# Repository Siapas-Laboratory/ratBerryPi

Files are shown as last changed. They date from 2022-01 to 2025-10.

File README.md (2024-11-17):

# ratBerryPi
A Raspberry Pi based system for controlling liquid-reward delivery and basic cue presentation for animal behavioral experiments. The system is customizable and programmable with Python. Functionality is provided for interfacing with the hardware either locally on the Pi or remotely from a client device. We also provide an additional Python package, [pyBehavior](https://github.com/nathanielnyema/pyBehavior) which contains tools for building GUIs to interface with the system (remotely or locally) and for developing behavioral protocols which leverage the hardware.

## Overview
ratBerryPi was built for the general class of behavioral paradigms that involve an animal collecting a liquid reward from one of many end points. The system is built around a modified version of the open source [Poseidon Syringe Pump](https://pachterlab.github.io/poseidon/), which we use to supply fluid as reward to any of multiple reward end-points via a manifold of 3-way stopcocks with luer connectors and an array of media isolation solenoid valves. One valve on the manifold is connected to a reservoir which can be used to intermittently refill the syringe without unloading and reloading it. The reward end-points in this system are modules that are each fitted with a lickometer, speaker and LED. The reward modules plug into a central interface that sits as a HAT on the Raspberry Pi controlling the system. In theory, up to 32 modules can be connected to a given pi by stacking 4 interface HATs. All peripherals are accessible and programmable through a Python class we've defined called the RewardInterface. Users may access this interface either remotely or locally (see [Usage](#usage)). The codebase was developed with flexibility and configurability in mind such that skilled users may modify the hardware and software to meet their needs (see [Software Overview](docs/software_overview.md) and [Hardware Overview](docs/hardware_overview.md)).

[***PICTURE HERE***]

## Getting Started
In this repository we provide stl files for our modified version of the syringe pump and manufacturing files for printing our custom PCBs which control all peripherals. For build instructions use the following links:

- [Hardware Assembly](docs/hardware_assembly.md)
- [PCB Ordering](docs/pcb_ordering.md)
- [Electronics Assembly](docs/electronics_assembly.md)

### Software Installation - (Raspberry Pi)
Clone this repository then follow these steps to setup a raspberry pi for use with ratBerryPi:

1. If you haven't already, install miniforge3 by downloading using the appropriate installer which can be downloaded from [here](https://github.com/conda-forge/miniforge?tab=readme-ov-file#download).

2. Create a conda environment using the environment.yml file provided in this repo and activate it by running the following from the project directory:

```
conda env create -f environment.yml
conda activate ratBerryPi
```

3. Run the following to configure the pi for use with the adafruit-blinka library (modified from [here](https://learn.adafruit.com/circuitpython-on-raspberrypi-linux/installing-circuitpython-on-raspberry-pi)):

```
pip install --upgrade adafruit-python-shell
curl https://raw.githubusercontent.com/adafruit/Raspberry-Pi-Installer-Scripts/master/raspi-blinka.py| sudo -E env PATH=$PATH python -
```

4. After the reboot, re-navigate to the project directory, re-activate the conda environment and run the following to finish the installation:

```
pip install '.[pi]'
```

#### If using with pyBehavior
If interfacing with ratBerryPi through [pyBehavior](https://github.com/nathanielnyema/pyBehavior) directly on the pi you can install pyBehavior in this environment by first cloning the pyBehavior repo and then running the following from the cloned repository:

```
conda env update --name ratBerryPi --file environment.yml
pip install .
```

### Software Installation - (Client Device)
As detailed in the Usage section below, one mode of operation of this system is to configure the raspberry pi that is connected to the hardware to function as a server that clients may connect to in order to trigger rewards or cues. For this to work, the ratBerryPi python package must also be installed on the client device. To install ratBerryPi on a client device, simply clone this repository, navigate to the cloned repository and run `pip install .` while any desired virtual environment is activated.

## Usage
There are 2 main modes of operation for the ratBerryPi. The Raspberry Pi can be configured as a server that clients on other machines may connect to in order to run commands through the RewardInterface class. Alternatively, one may write a Python program on the raspberry pi itself which creates an instance of the RewardInterface class and invokes methods of the class to run a behavioral protocol.

### Local RewardInterface

Users may interact with the ratBerryPi through an instance of the RewardInterface class as follows:

```python
from ratBerryPi.interace import RewardInterface

rpi = RewardInterface()
rpi.start()

# do something

rpi.stop()
``` 

If nothing is passed to the constructor of the class, rpi will be an instance of the RewardInterface configured according to the config file located at ratBerryPi/config.yaml in the cloned repo (see [Configuration](docs/software_overview.md/#configuration); you shouldn't need to alter the config if using the hardware we provide). The constructor can also optionally take the following parameters which can be ignored by most:

- `on` (threading.Event) - threading event object that can be used to synchronize start and stopping the interface with any other threads which may be running in your program (for an example see `ratBerryPi/remote/server.py` where we use an event to stop the interface when we stop the server)
- `config_file` - path to an alternate config file
- `data_dir` - path to a directory to save any data produced by the interface after calling the `record` method. If not specified all data is saved at `~/.ratBerryPi/data`

Several instance methods are provided through `rpi` which allow the user interact with the hardware. For a full list of these methods see the help documentation for the RewardInterface class. This documentation can be accessed from a python terminal as follows:

```python
from ratBerryPi.interface import RewardInterface
help(RewardInterface)
```

### Server-Client Mode
We provide a cli for creating either a server or a cli via the command `ratBerryPi` which can be called from the command line. To start a server on the raspberry pi, simply run the command `ratBerryPi server`. This will expose a port on the raspberry pi for clients to connect to for running commands through the reward interface and broadcasting information about the state of the device.  By default it will bind port 5562 but this can be set as needed by passing the arguments `--port`. If using an interface other than the reward interface.

Users may connect to the server programmatically by first creating an instance of the `Client` class defined in `client.py`. For example:

```python
from ratBerryPi.client import Client

host = '123.456.789' # raspberry pi ip address
port = 5562

cl = Client(host, port)
```

Once you've created the client, the 2 most important methods of this class are `run_command` and `get`. 

- `run_command` provides an interface to run commands remotely through the interface running on the server. It takes as input 2 positional arguments, the first of which is a string indicating the name of a method in the interface class to run. The second argument is a dictionary specifying keyword arguments for this function. For information on available methods see the help documentation for the RewardInterface as discussed above

- `get` provides an interface to retrieve state information from the reward interface; it takes as input a string indicating the attribute of interface class you would like to get the value of. This string should be everything that would come after the period when directly accessing an instance of the interface class. for example, if we want the position of a pump named `pump1` when using the reward interface, the request would be `'pumps["pump1"].position'`.  

Both `run_command` and `get` further take as input an optional keyword argument `channel` which allows the user to specify the name of a 'channel' for communicating with the server. These channels are simply an abstraction for a connection to the server and allow users to isolate certain types of requests to avoid cross talk. For example, I may want to create an app using the reward interface where it would be useful to spawn a thread in the background to continuously monitor the position of the pump so I can print it for the user to see. It would be useful in this case to create a new channel specifically dedicated to these requests. Behind the scenes the server keeps these channels isolated by spawning separate threads for handling requests made on different channels. To create a new channel simply use the method of the client class `new_channel` which takes as input one positional argument which is the name of the new channel.

To start a client via the cli simply run the command `ratBerryPi client`. The default behavior of this method is to connect to a server hosted locally. If you would like to connect to a ratBerryPi server from a separate client device provide the `--host` argument as well as the `--port` argument if the server is being hosted on a non-default port. This should launch a cli where you can enter method names from the reward interface as commands followed by argument names and associated arguments separated by spaces. For example, if you wanted to run the trigger_reward method for a 1 mL reward on module1,  you would enter:

```
trigger_reward module module1 amount 1
```

There are 2 special commands: `get` and `exit`. `exit` will close the connection to the server and stop the cli. `get` is the cli equivalent to the get method described above.

## Operating the Pump and Manifold
The primary interface to the pump and valves is meant to be in software, however we provide some features to control the pump and fill valve manually to help with loading and unloading a syringe. Specifically, there are 3 buttons on the interface HAT that users should be familiar with: the flush button, the reverse button, and the fill valve button. The flush button allows you to manually advance the pump carriage sled forward. The reverse buton allows you to manually advance the pump carriage sled backwards. The fill valve button allows you to manually toggle the valve that goes to the reservoir (i.e. when the fill valve button is pressed this valve is open). In theory it is also possible to manually turn the lead screw to move the carriage sled if the pump is powered down (i.e. the 12V power supply to the interface board is unplugged) however we strongly discourage operating the pump in this way. In general it should be noted that whenever the 12V power supply is unplugged or the pump is unplugged, you should re-calibrate the pump before using it for anything. To do this you can use the calibrate method ot the Reward Interface.

### Filling the lines
For optimal performance, before triggering any rewards, all lines for reward delivery must be filled with the solution to be delivered to the reward ports. The key to doing this properly is making sure there are as few air bubbles in the lines as possible. We provide a method through the RewardInterface called fill_lines which automatically fills the lines. We strongly recommend users call this method before triggering any rewards. In the pyBehavior PumpConfig widget there is a button available that calls this method. Prior to running this method, be sure to pre-fill a syringe, load it in the pump, and make sure the reservoir is full. We've also found it useful to manually push some fluid to the reservoir while the pump is loaded with the full syringe before calling `fill_lines`. ***NOTE: If you do this make sure to hold open the fill valve with the fill valve button*** Importantly, this process can only work if the syringe used for filling the lines has at least as much volume as the dead volume leading up to the reservoir. Depending on the use case, it may even be in the user's best interest to use a fairly large syringe (about 30 mL) to fill the lines and switch to a more precise syringe for the experiment itself.

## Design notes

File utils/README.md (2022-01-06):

# Desi_FallRotation-
Code + documentation of Desi's fall rotation in the Siapas Laboratory. Project entailed developing initial steps of creating a new training chamber using python, raspberry pi, stepper motor, speaker, and other related components / pieces. 

## IRBeam.py
simple piece of code that detects whether there is a break in the IR beams. There are two approaches included in the file, as noted in the comment - using the event detection function (versus the while loop approach) would be the best method to achieve flexibility in where to place event detection in the other files (especially main.py) 

### functions
def break_beam_callback(channel):
* channel = meaningless parameter, it is there so that the function can be called currently from GPIO.add_event_detect

## audio.py

generates sine wave based on certain parameter values:
* frequency (Hz)
* duration (ranges from 0.0 to <300 seconds)
* volume (ranges from 0.0 to 1.0) 
* sample rate (samples per second) 

outputs the sine wave through the audio port on the raspberry pi 

### functions 

def sine_tone(self, frequency, duration, volume=1, sample_rate=22050)
* frequency = frequency of sound output in Hz 
* duration = length of the audio 
* volume = volume of sound output, automatically set to 100% volume. 
* sample rate = samples per second, automatically set to 22050

## syringe.py 

in reality this controls the movement of the stepper motor, and there are different 
values that are set to output the desired amount.

* units     microliters or milimeters 
* amount    integer value of amount of chosen units to output 
* syringeType   3 mL or 1 mL syringe 
* stepDelay     Would not recommend changing, but it is the delay between one movement of the motor to the next 
* stepType    "Full", "Half", "1/4", "1/16", "1/32". Automatically set to "Half".
* loopNumber    Number of loops during calibration 

### functions 

def calculateSteps(self)
calculates steps based on amount, units, syringeType, stepType 

def syringeGPIOInit(self)
intializes GPIO pins of the syringe amd sets it up 

def pulseForward(self)
pulses the motor forward by just the number of steps 

def cleanupGPIO(self)
resets the GPIO pins 

## main.py
main interface file which references audio and syringe files. This is where the menu interface is built, and where calls to different functions are made. By building the other files using an object oriented programming approach, the main file can call functions on a syringe object or audio object. To run this file, navigate to its location in a terminal and simply run the file 

python main.py 

### functions 

def highTone()
plays sound output at frequency set for the high tone 

def lowTone()
plays sound output at frequency set for the low tone 

def settingsMode()
enters setting mode to adjust different values set up for the audio or syringe.
this is not as well developed. 

def experimentMode()
enters experiment mode where user has option to pulse syringe, play high tone and low tone, or enter settings mode

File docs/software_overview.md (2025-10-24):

# Software Overview
## Architecture
RatBerryPi consists of 3 layers of abstraction: the reward interface, reward modules and resources. The interface orchestrates use of all modules and resources. Resources are considered to be devices such as a syringe pump or solenoid valve that may or may not be shared accross modules. Modules are collections or resources. Importantly, the module must have associated to it a valve which can be opened to direct the flow of fluid to it. In the default use case, the interface has associated to it a set of pumps which several reward modules share. Each module has a valve, an led, a lickometer and a speaker associated to it.

**Technical Notes**
#TODO: add some info here about how the multi-speaker control is implemented in hardware and what this means for how the speakers are controlled and also the lickometer bus

## Configuration
This package includes a default configuration file `default-config.yaml` which reserves GPIO pins and pins on the GPIO expander to control up to 8 of our custom modules. Users may specify a custom configuration file by creating a file called `.ratBerryPi-config.yaml` and placing it in the home directory of the pi (i.e. the file should have path `~/.ratBerryPi-config.yaml`). At a minimum, the configuration must specify the fields `modules` and `pumps`. `modules` should should have sub-fields corresponding to module names and each sub-field should have corresponding sub-fields with configuration parameters for that module. Pump parameters should be specified equivalently under `pumps`. Below we detail necessary parameters for pump and module configuration:

### Module Configuration
Modules may be considered either using presets or from scratch. When configuring modules from scratch, users must specify the module `type` along with any relevant parameters for that module type. Default modules, for example, are specified by "type: DefaultModule" and require the following parameters

* `LEDPin`: GPIO pin that controls this module's LED
* `lickPin`: GPIO pin monitoring licks on this module
* `SDPin`:  GPIO pin that gates audio played on this module's speaker
* `valvePin`: GPIO pin that will control the valve that gates reward delivery to this module
* `dead_volume` *(optional)* : dead volume in tubing leading up to the module
* `lickBusPin`: GPIO pin that reads the interupt signal from the bus associated to this lickometer
* `pump` - the name of the pump feeding into this reward module

Note that GPIO pins on the GPIO expander must be specified by the expander's hexadecimal address first followed by the pin name (e.g `0x21:GPA0` for pin A0 on the expander at address 0x21). As noted below, `pump` and `valve_pin` are required arguments for all module types. 

Users may specify a `preset_name` to configure a module according to preset pin mappings specified in `presets.yaml`. Any parameters not specified in the preset must be specified in the config file.

#### Custom Modules
For users that would like to create custom reward modules you will need to define the module under the `ratBerryPi/interfaces/reward/modules` folder by sub-classing the BaseRewardModule class (see `ratBerryPi/interfaces/reward/modules/default.py` for an example). Importantly, the user must define a method `load_from_config` in the sub-class which should take as input a dictionary with configuration parameters for the module (such as pin mappings) and instantiate any resources the module needs as necessary. This dictionary will come from the `config.yaml` file. For any custom module type, users must specify a pump and valvePin.

### Pump Configuration

When configuring a pump, one must specify the following fields

* `port` : usb port address for communicating with the pico that controls the pump
* `lead` : lead of the lead screw in cm
* `syringeType` *(optional)* -The type of syringe that will be loaded on the pump by default. Current options include: BD1mL, BD5mL, BD10mL, BD30mL, BD50/60mL. Note, these options refer to keys in a dictionary called `syringeTypeDict` defined in the `Syringe` class in `pump.py`. Users may add additional syringes by adding new entries to this dictionary with the inner diameter of a given syringe and the maximum length the syringe can be withdrawn to when loaded on the pump (in cm).
* `fillValvePin` *(optional)* - A pin on the raspberry pi to control a valve attached to reservoir. This valve, if specified, will be used to allow fluid to be drawn into the syringe from the reservoir

### Plugins

Users may optionally specify resources that are not attached to a module which we refer to here as "plugins". Under `plugins` the user should specify unique names for each individual plugin used in the device. Under these names the user should further indicate any relevant key word arguments that would be needed to instantiate the plugin's associated class

 ## Developer Notes
 We encourage users to clone the repository and customize the code to their needs. To define a new resource sub-class the BaseResource class in the ratBerryPi/resources folder and define the class in a file in the same folder. Note, in the interest of thread safety, the BaseResource class when initialized has an attribute `lock` which is a re-entrant lock (see [here](https://docs.python.org/3/library/threading.html#rlock-objects) for details). We recommend developers to use this lock as a way to reserve resources in case multiple clients try to access it. To create a new module simply sub-class the BaseModule class under ratBerryPi/modules and define the class within a file you create in this same folder. Importantly this BaseModule class is an abstractbaseclass which expects the user to define a load_from_config method in the subclass which will configure the module instance using a config specified as a dict which is loaded from each module field within the config file. For an example see the default module. After making any changes you can reinstall the ratBerryPi by navigating to the root directory of the repo and running `pip3 install .`

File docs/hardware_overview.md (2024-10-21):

## Electronics Overview
The 2 main hardware components of the system are the interface and the modules. The interface is a HAT that sits on a raspberry pi, but often we may refer to the entire unit as the interface. Similarly when we refer to modules we are usually referring to the entire reward module unit consisting of all attached devices (lickometer, speaker, and LED). At it's core, however, the reward module is controlled by a PCB that usually is packaged with the module. This PCB has the main electronics needed to operate all devices. The interface functions as a hub for all modules to plug into and offers some additional features which we will describe below.

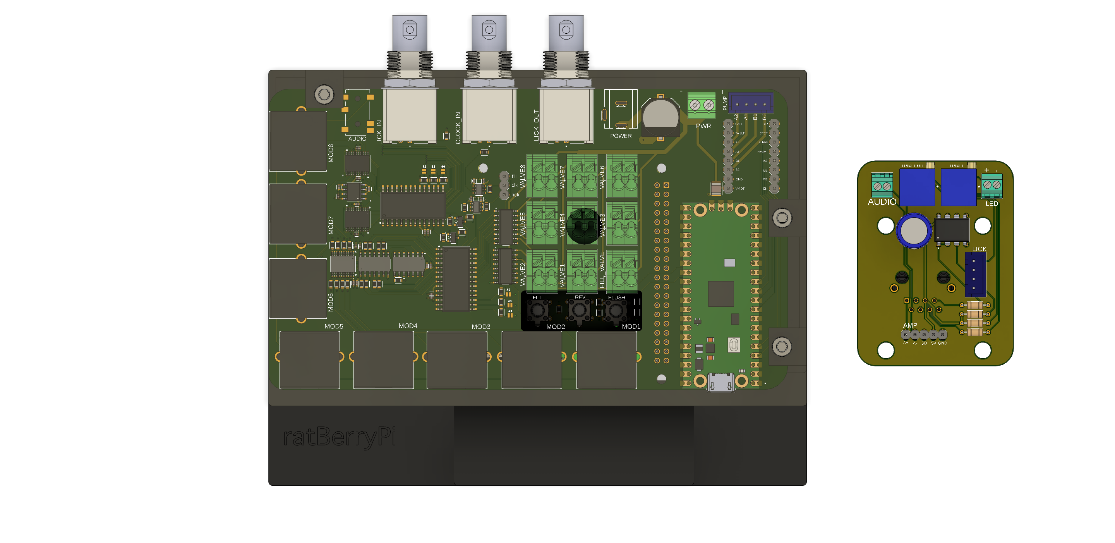
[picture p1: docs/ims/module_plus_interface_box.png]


### User Selectable I/O
Most digital I/O in the ratBerryPi system is handled through extended GPIOs provided by 2 I2C interfaces on each interface HAT. The effect is that most GPIOs on the Pi itself remain available for users program as they wish. The caveat is that there are 2 signals that could not be allocated to a slot on the I2C interfaces due to space constraints and another that needs to be read by a GPIO on the pi itself for performance reasons. Instead of hardwiring these signals to any GPIOs on the Pi we allow the user to configure them as needed. The benefit of this setup is that in the event you need to stack interface HATs, you can select different pins for each HAT as needed. The that need to be assigned to GPIOs are as follows:

* **Fill Valve Software Control** - This allows the user to set the state of the valve leading up to the reservoir in software (see [Fluid Delivery System](#fluid-delivery-system))
* **Clock Input** - see [Clock Signal](#clock-signal)
* **Lick Bus Interrupt** - all lick signals on a given interface HAT are read on the same bus of one of the I2C interfaces. There is an interrupt pin on this bus that we've configured to be LOW normally but write HIGH when when a rising edge is detected on any pins on the bus. This interrupt signal needs to be read by a designated GPIO pin on the pi itself for any licks to be registered. The idea is when this GPIO pin on the pi reads a HIGH value ratBerryPi polls the I2C interface to see which GPIO on the bus caused it. For those curious, the reason for this configuration is that the gpiozero, the library we use in python to control the GPIOs, provides an interface to configure callback functions to run very quickly on the rising or falling edge of a digital signal. We use a separate library to program the I2C interface and this library does not offer this functionality. As such the best you would be able to do otherwise is to spawn a python thread that continuously polls the state of the GPIOs on the I2C interface.

### OR'd Licks
In many setups there may be a central unit that you want to use to timestamp all events that occur during experiments. In such scenarios we offer 2 ways of getting timestamps of lick events on the clock of your timestamping unit. One is through the **CLOCK IN** port that we will discuss later. The other is through the **LICK OUT** port. This port broadcasts a 5V TTL signal which represents the result of a hardware "OR" operation over all modules on the interface. This is implemented in hardware by a cascade of pairwise logical OR gates where the inputs are the digitized lick signals. Importantly, at the last step, the OR's lick signal from the modules on a given interface is OR's with any licks provided through the **LICK IN** port. This port takes 5V logic. The result is that if you stack interface HATs or use multiple interfaces in a given setup, you can chain together multiple interfaces and the OR'd lick output of the last interface will be the OR'd licks over all modules. 

### Clock signal
One can use the software interface provided through this repo to log relevant events that occur. One method of synchronizing this datastream with datastreams on other systems is a method detailed in the OpenEphys documentation. Briefly, the idea is to timestamp a common clock signal on all devices. This signal is some digital signal with known temporal structure that can be used to map timestamps on all devices to a common clock. We support use of such a system with the **CLOCK IN** port. Users may plug such a clock signal (5V logic) into this connector and an event called clock will be logged with respect to the pi's system clock on the rising edge of all pulses detected on this port. Considering all other events logged through ratBerryPi are also logged against system clock, you can use the timestamps of these clock events to remap system clock of the pi against a common clock for all relevant devices.

### Stackable HATs
This feature has not been tested as yet, but in principle the interface HATs are designed to be stackable. When stacking HATs, the following should be taken into consideration:
* Be sure to daisy chain 12V power to all stacked HATs. The PWR screw terminal is there for this purpose
* Update the I2C address on all stacked HATs to be unique. This can be done using the address select jumpers (A0-A2 and B0-B2) on the interface HAT. Jumping any pads together sets that bit in the I2C address to 1. By default, (A0=0, A1=0, A2=0) and (B0=1, B1=0, B2=0).

### Audio
All modules have a screw terminal to plug in a speaker. Audio is provided to the modules from a single audio source which can be plugged in through the headphone jack on the HAT. This audio source can either be an audio HAT (specifically the [Innomaker HIFI DAC Pro HAT](https://www.amazon.com/Raspberry-DAC-Pro-ES9038Q2M-Resolution/dp/B0B2DJZTSF)) or the pi itself if using a Raspberry Pi 4. Importantly if using the Pi audio, you will need to amplify this audio on the level of the module. For this you can use the PAM8302 Class D Amplifier. There is a designated spot on the module PCB for it. Instead of plugging the speaker into the AUDIO screw terminal, you can use the output of the PAM8302. 

It's worth noting that because audio in this system is provided by a single source, it would not be possible to play different audio on different speakers. You may however, play the same audio on a subset or one of many speakers. This is handled by an onboard analog switch which directs the audio input to the desired end point.

## Fluid Delivery System
They main components of the fluid delivery system are the syringe pump, the valves that lead up to each reward module, the valve that leads up to the reservoir (the fill valve), the reservoir and the manifold of 3-way stopcocks that all valves are mounted to. 

![alt text]()

Many of these components are there to enable automatic refilling of a syringe without the need for unloading, However, the fundamental function of the system, namely delivering reward to a specified module, is supported primarily by the valves for each module and the pump. In practice, this is what a reward delivery looks like in this system:

1. A GPIO pin is set to a HIGH state in order to open the valve for a specified module
2. We wait a set period of time for the valve to actually open.
3. The pump advances to perfuse the requested reward amount.
4. We wait for a set period of time to ensure the entire reward amount has made it to the module (this is necessary because any compliance in the lines means that reward delivery is not instantaneous)
5. The GPIO pin associated to the valve is set to LOW to close the valve.
6. We wait to make sure the valve is closed.

Whenever we need to refill the syringe this is accomplished by closing all valves except the fill valve, opening the fill valve, and running the pump in reverse to draw fluid from the reservoir into the syringe. We added a clamp to the pump to allow the syringe to be secured in place to avoid significant slack when switching between reversing and advancing the pump. However, to be safe, a small volume is pumped to the reservoir before any reward delivery after the pump was in reverse.

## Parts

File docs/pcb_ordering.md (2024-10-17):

# Guidelines For PCB Ordering
Our manufacturer of choice for all PCB's to date has been JLCPCB. The manufacturing files provided are geared towards a smooth checkout process through JLCPCB. There are 2 types of PCBs that need to be built for this project: the interface HAT and the module PCB. Our recommendation is to get as much of the interface HAT assembled by JLCPCB as possible because there are many components and many of them are surface mount. The module PCBs on the other hand can be assembled as needed, and as such it should be sufficient (and more cost effective) to order these boards unassembled and solder the components to them yourself.

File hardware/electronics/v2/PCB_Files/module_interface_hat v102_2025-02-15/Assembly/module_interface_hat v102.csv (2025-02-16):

Qty | Comment | Designator | Footprint | JLCPCB Part #
10 | 0.1µF | C3, C4, C5, C10, C12, C17, C20, C21, C22, C23 | CAPC1005X60 | C361203
9 | 100kΩ | R3, R7, R8, R9, R10, R11, R12, R13, R14 | RESC1608X60 | C2139679
1 | 100µF | C2 | CAPAE1030X1050N | C2843277
1 | 100µF | C1 | CAPC3225X135 | C6120014
14 | 10kΩ | R19, R20, R21, R22, R23, R24, R26, R28, R29, R30, R31, R36, R38, R39 | RESC1608X60 | C2139679
4 | 10µF | C9, C11, C18, C19 | CAPC1005X60 | C15525
1 | 1727010 | PWR | 1727010 | C89123
9 | 1984963 | FILL_VALVE, VALVE1, VALVE2, VALVE3, VALVE4, VALVE5, VALVE6, VALVE7, VALVE8 | PHOENIX_1984963
3 | 1µF | C6, C7, C8 | CAPC1005X60 | C3015153
13 | 22kΩ | R1, R2, R4, R5, R6, R15, R16, R17, R18, R32, R33, R34, R35 | RESC1608X60 | C209074
2 | 50Ω | R25, R27 | RESC1608X60 | C830222
2 | ADG1434YRUZRU_20_ADI-L | U9, U10 | RU_20_ADI-L | C408906
1 | B4B-XH-A | PUMP | B4B-XH-A | C594232
4 | BSS138 | Q1, Q2, Q3, Q4 | SOT95P240X111-3N | C78284
3 | CONBNC002 | CLOCK_IN, LICK_IN, LICK_OUT | LINX_CONBNC002 | C2837588
1 | DC-005-2.5A-2.0 | POWER | DC-005-2.5A-2.0 | C319099
8 | HC-RJ45-5JA-1-4 | MOD1, MOD2, MOD3, MOD4, MOD5, MOD6, MOD7, MOD8 | HC-RJ45-5JA-1-4 | C3000174
1 | MAX1044ESA-T | U11 | SOIC127P600X175-8N | C140450
2 | MCP23017 | IC1, IC2 | SOIC127P1030X265-28 | C47023
1 | PINHD-1X3 | JP3 | 1X03 | C3327863
2 | PINHD-1X8 | JP1, JP2 | 1X08 | C5224027
1 | PJ-3420-A-SMT | AUDIO | PJ-3420-A-SMT | C319102
1 | SC0915 | U2 | MODULE_SC0915 | C7203002
3 | SKHHQYA010 | FILL_BTN, FLUSH, REV | SKHHQYA010 | C470257
1 | SN74HCS244QPWRQ1TSSOP20_4P4X6P5_TEX | U1 | TSSOP20_4P4X6P5_TEX | C2864779
2 | SN74HCT32DRD14 | U3, U4 | D14 | C6781
2 | ULN2003ADRD0016A_N | U5, U6 | D0016A_N | C7512

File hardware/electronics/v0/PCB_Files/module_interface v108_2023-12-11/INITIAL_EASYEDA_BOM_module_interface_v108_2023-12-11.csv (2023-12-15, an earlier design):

ID | Name | Designator | Footprint | Quantity | Manufacturer Part | Manufacturer | Supplier | Supplier Part | Price
1 | B4B-XH-A | PUMP | B4B-XH-A | 1
2 | HIF3FC-16PA-2.54DSA_71_ | SD,LED,PUMP_CTL,VALVE_CTL | SHDR16W56P254_2X8_2782X850X950 | 4
3 | CONBNC002 | LICK_OUT,LICK_IN | LINX_CONBNC002 | 2
4 | 22kΩ | R1,R2,R4,R5,R6 | RESAD724W46L381D178B | 5
5 | 61200621621 | J3 | 61200621621 | 1
6 | ULN2003ADRD0016A_N | U5,U6 | D0016A_N | 2
7 | SN74HCT32DRD14 | U3,U4 | D14 | 2
8 | 1727010 | REV_BTN,FILL_VALVE_BTN,FLUSH_BTN,VALVE1,VALVE2,VALVE3,VALVE4,VALVE5,VALVE6,VALVE7,VALVE8,FILL_VALVE | 1727010 | 12
9 | HC-RJ45-5JA-1-4 | MOD1,MOD2,MOD3,MOD4,MOD5,MOD6,MOD7,MOD8 | HC-RJ45-5JA-1-4 | 8
10 | PJ-3420-A-SMT | AUDIO | PJ-3420-A-SMT | 1
11 | DC-005-2.5A-2.0 | POWER | DC-005-2.5A-2.0 | 1
12 | X6511WVS-13H-C60D48R2 | U$12 | X6511WVS-13H-C60D48R2 | 1
13 | CAPAE830X1050N | C2 | CAPAE830X1050N | 1
14 | PINHD-1X8 | JP1,JP2 | 1X08 | 2

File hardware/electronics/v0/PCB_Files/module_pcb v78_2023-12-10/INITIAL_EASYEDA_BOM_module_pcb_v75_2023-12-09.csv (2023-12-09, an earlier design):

ID | Name | Designator | Footprint | Quantity | Manufacturer Part | Manufacturer | Supplier | Supplier Part | Price
1 | 2828XX-2282834-2 | LED | TERMBLK_254-2N | 1
2 | B4B-XH-A | LICK | B4B-XH-A | 1
3 | PINHD-1X5 | AMP | 1X05 | 1
4 | 1kΩ | R4 | PV36P | 1
5 | 220Ω | R1 | RESC1608X60 | 1
6 | 22kΩ | R2 | RESC1608X60 | 1
7 | 68Ω | R3 | RESC1608X60 | 1
8 | 5557969-1 | J1 | TE_5557969-1 | 1

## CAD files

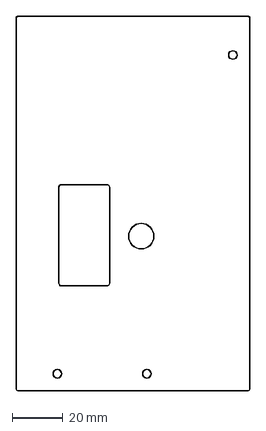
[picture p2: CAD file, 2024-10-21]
hardware/3Ddesigns/dxf/interface_box_lid.dxf
92.4 x 148.1 mm

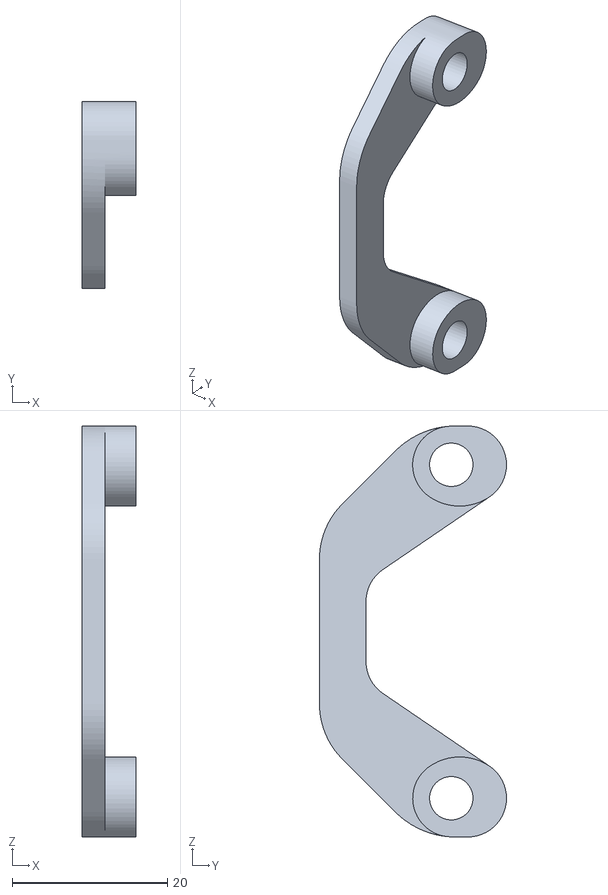
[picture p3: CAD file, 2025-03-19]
hardware/3Ddesigns/stl/pump_syringe_clamp.stl
7.00 x 24.1 x 53.0

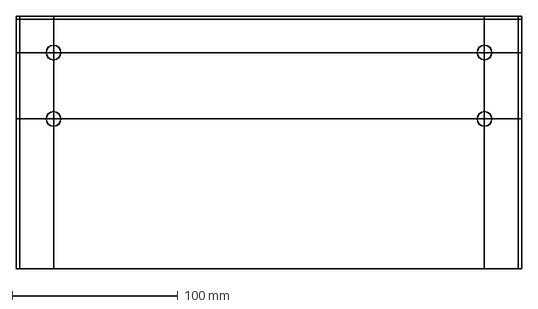
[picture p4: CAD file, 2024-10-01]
hardware/3Ddesigns/dxf/wall_sheet_6x12in.dxf
304.8 x 152.4 mm

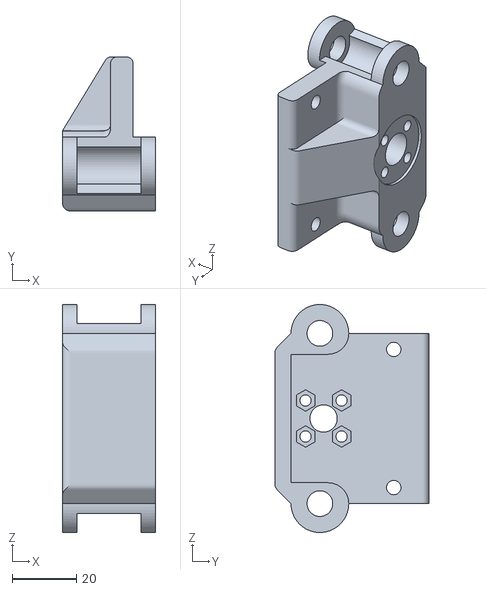
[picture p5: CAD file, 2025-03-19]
hardware/3Ddesigns/stl/pump_carriage_sled.stl
29.0 x 48.0 x 71.0

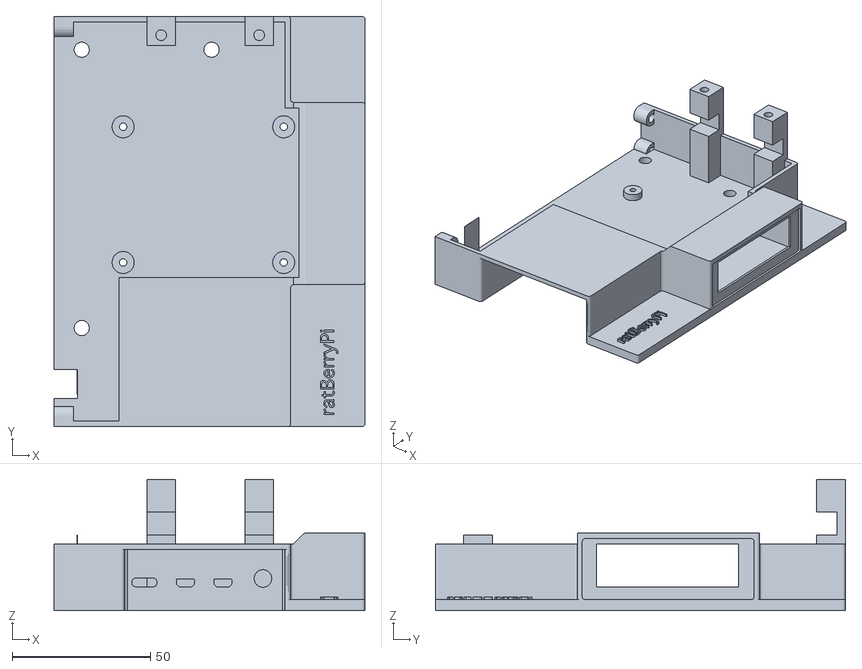
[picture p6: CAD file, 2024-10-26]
hardware/3Ddesigns/stl/interface_box_base.stl
112.3 x 148.1 x 47.4

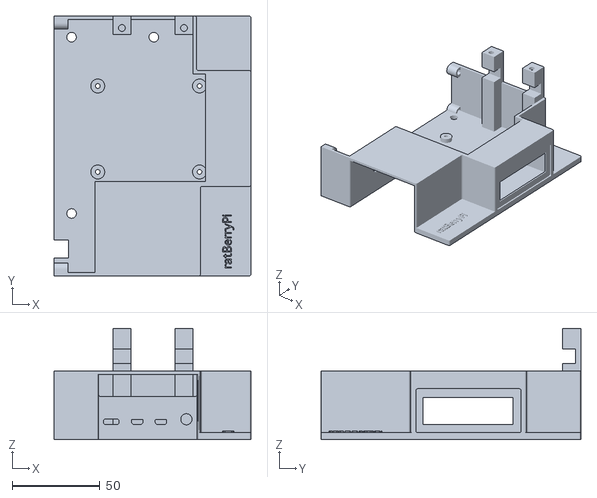
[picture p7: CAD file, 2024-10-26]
hardware/3Ddesigns/stl/interface+audio_box_base.stl
112.3 x 148.1 x 63.4

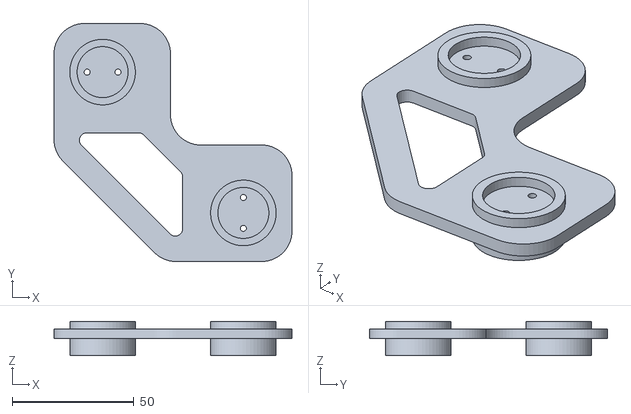
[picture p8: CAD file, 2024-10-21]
hardware/3Ddesigns/stl/2valve_mount.stl
97.9 x 97.9 x 14.0

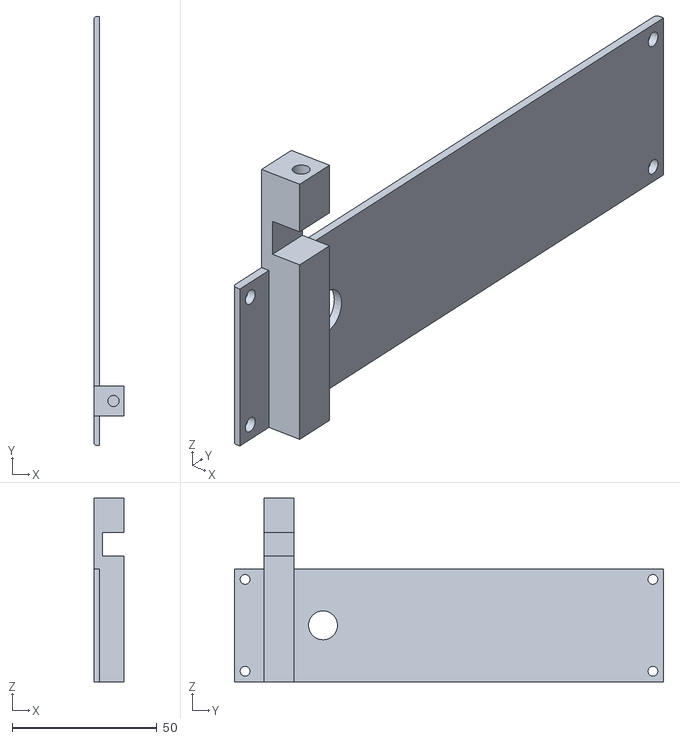
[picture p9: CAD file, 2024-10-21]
hardware/3Ddesigns/stl/interface+audio_box_back.stl
10.4 x 148.1 x 63.4

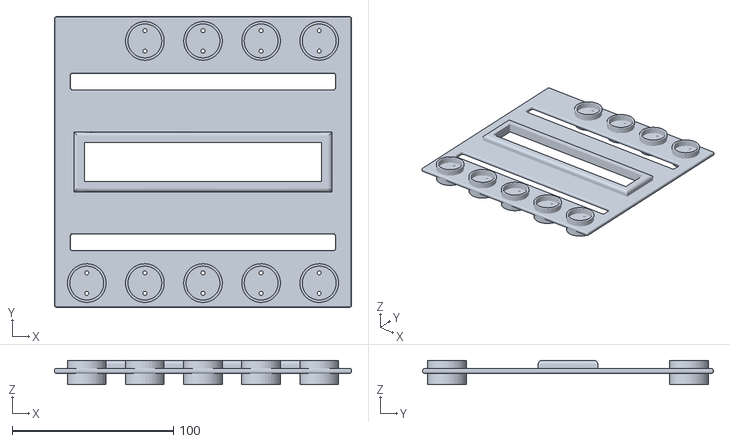
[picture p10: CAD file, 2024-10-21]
hardware/3Ddesigns/stl/manifold_mount.stl
184.0 x 180.0 x 15.0

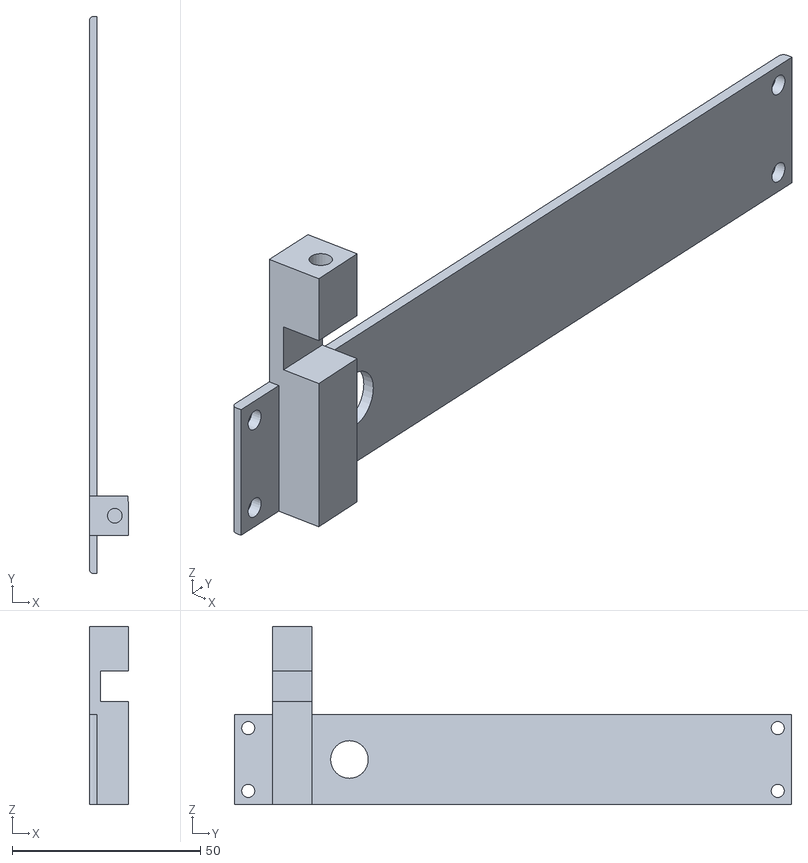
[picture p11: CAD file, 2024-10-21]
hardware/3Ddesigns/stl/interface_box_back.stl
10.4 x 148.1 x 47.4

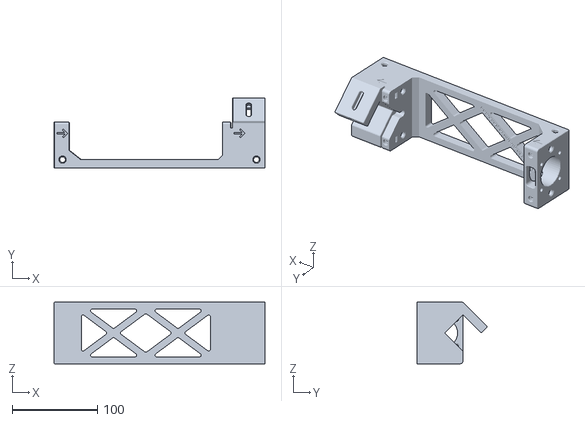
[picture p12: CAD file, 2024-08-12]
hardware/3Ddesigns/stl/pump_base.stl
247.0 x 82.3 x 72.0

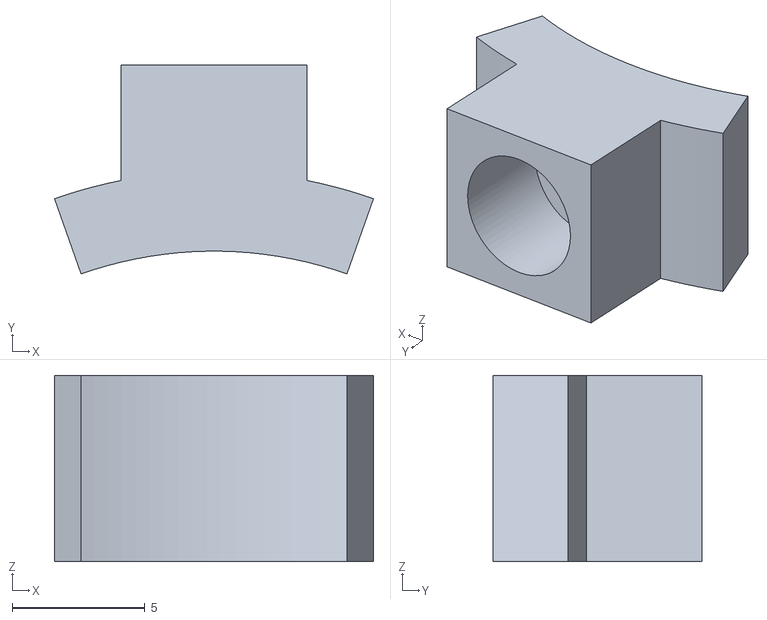
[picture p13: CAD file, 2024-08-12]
hardware/3Ddesigns/stl/pump_syringe_brace.stl
12.0 x 7.86 x 7.00

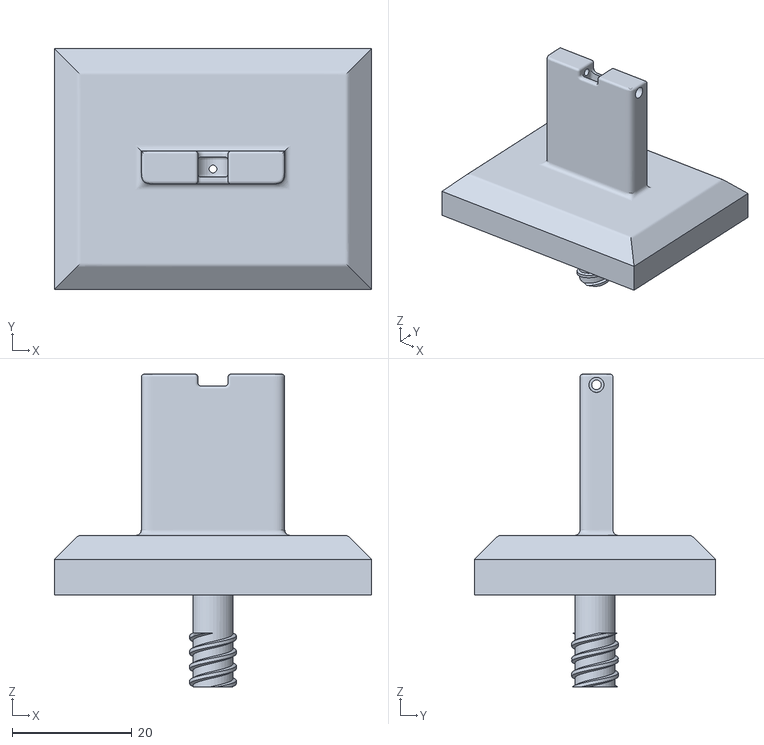
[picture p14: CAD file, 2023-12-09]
hardware/3Ddesigns/stl/lickometer_mouse.stl
53.0 x 40.3 x 52.4

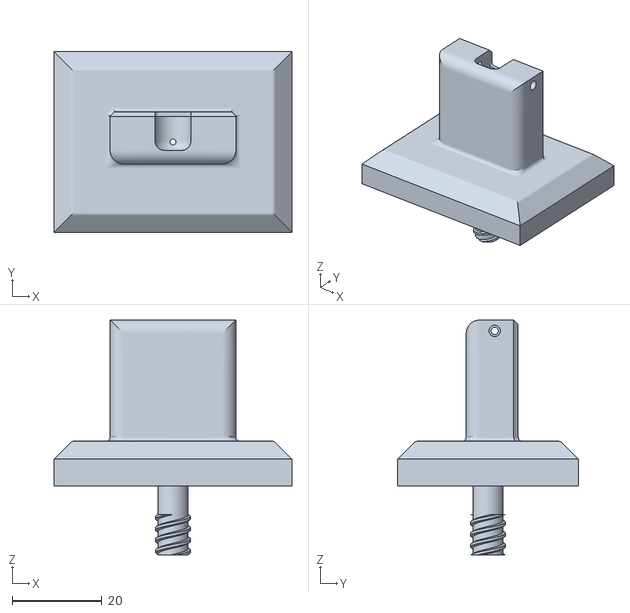
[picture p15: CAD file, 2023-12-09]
hardware/3Ddesigns/stl/lickometer_rat.stl
53.0 x 40.3 x 52.4

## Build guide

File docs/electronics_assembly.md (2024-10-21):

## Interface HAT
### Required Components
* Assembeld interface HAT + additional components that could not be assembled by the PCB manufacturer
* DRV8825 stepper motor driver (x1)
* Raspberry Pi (≥4)
* Male to Male Audio Cable (optional)
* [Innomaker HIFI DAC Pro Hat](https://www.amazon.com/Raspberry-DAC-Pro-ES9038Q2M-Resolution/dp/B0B2DJZTSF) (optional)
* 16 mm standoffs (x7) + nuts (x4)
* 10mm long M2.5 socket head screws
* Female to Female jumper
* USB cable
* printed [interface box](../hardware/3Ddesigns/stl/interface_box_base.stl) and [back](../hardware/3Ddesigns/stl/interface_box_back.stl) (if using the audio hat use this [box](../hardware/3Ddesigns/stl/interface+audio_box_base.stl) and [back](../hardware/3Ddesigns/stl/interface+audio_box_back.stl))
* M3 threaded inserts

### Assembly Steps
*Flashing Pump Code to the Pico*

In order to test out the electronics at the end we will need to have the pico firmware loaded. This is best done on a device other than the pi. We'll follow the steps detailed [here](https://randomnerdtutorials.com/programming-raspberry-pi-pico-w-arduino-ide/) to flash [pump control code](../pico/pump_control/pump_control.ino) to flash the code to the pi using the Arduino IDE.

1. Install the Arduino IDE on the device you will use to flash the code. 
2. Navigate to either Settings or Preferences depending on your OS.
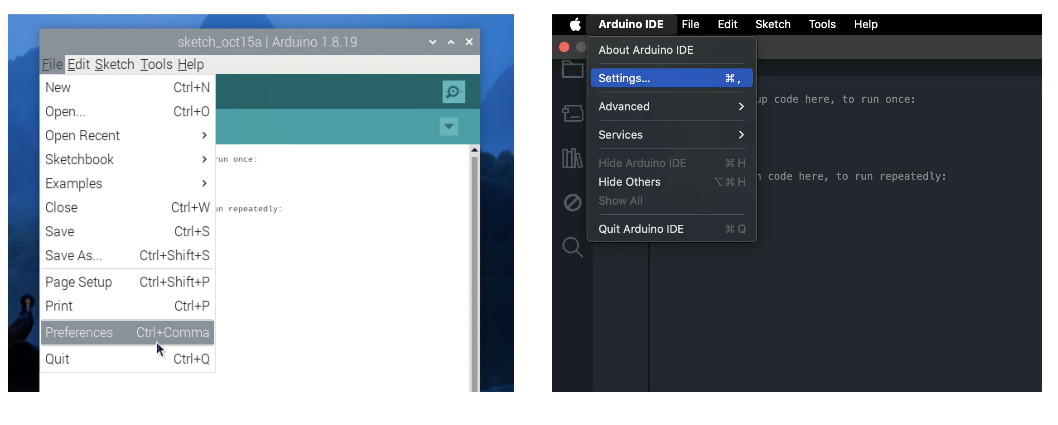
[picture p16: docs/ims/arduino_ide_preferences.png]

3. Enter the following URL in the "Additional Board Managers" field:
```
https://github.com/earlephilhower/arduino-pico/releases/download/global/package_rp2040_index.json
```
4. Go to **Tools > Board > Boards Manager**
5. Search for “pico” and install the Raspberry Pi Pico/RP2040 boards
6. Open the [pump control code](../pico/pump_control/pump_control.ino) in the IDE.
7. While the Raspberry Pi is unplugged, go to **Tools>Boards** and select Raspberry Pi Pico.
8. Hold the BOOTSEL button on the Pico while plugging it into your device.
9. Open the drop-down menu at the top and select "Select other board and port...". From here select the Rasperry Pi Pico as your board and "UF2 Board UF2 Devices" as the port. You may need to check the box that says "Show all ports"
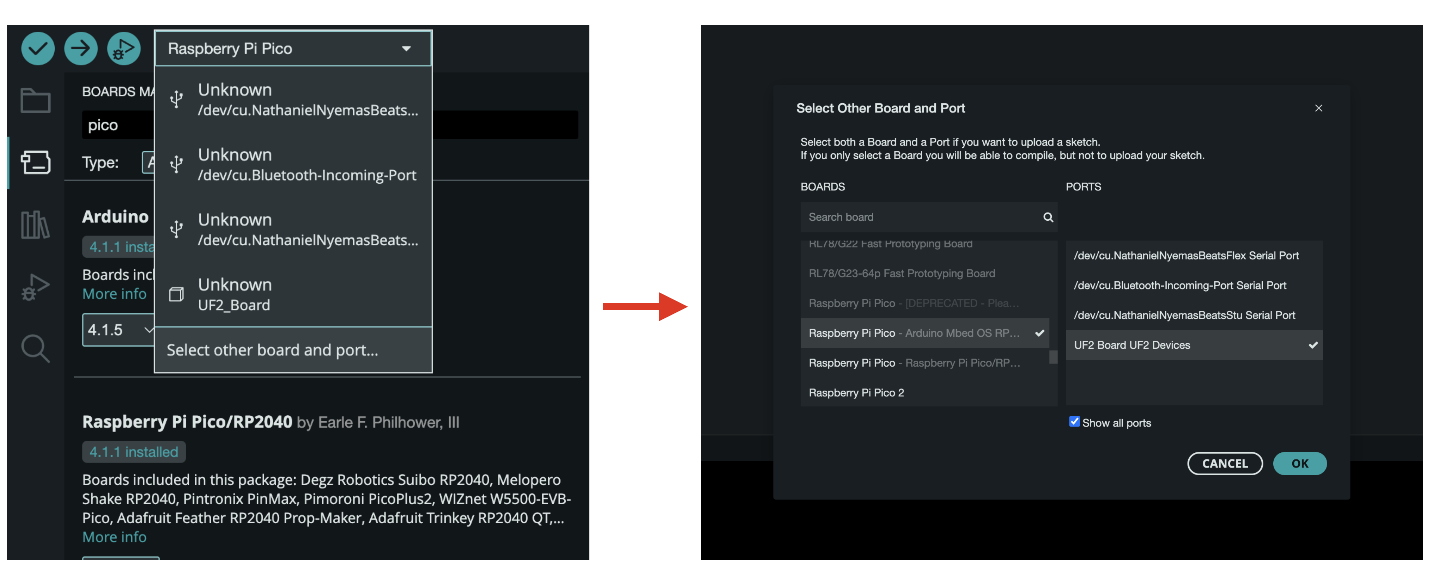
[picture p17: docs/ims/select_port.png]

10. Finally click the arrow at the top to flash the code to the Pico.


*Seting up the PCB*

1. Solder any components not soldered by the PCB manufacturer. The v1 PCB unfortunately does not have labels for all components on the board so we show the labels below. You can match component names to the part itself using the BOM for the PCB assembly job. Importantly, resistors are not labeled in this image as we generally recommend at least having these mounted by your manufacturer. (*NOTE: For all ICs the dot indicates the top left corner*)
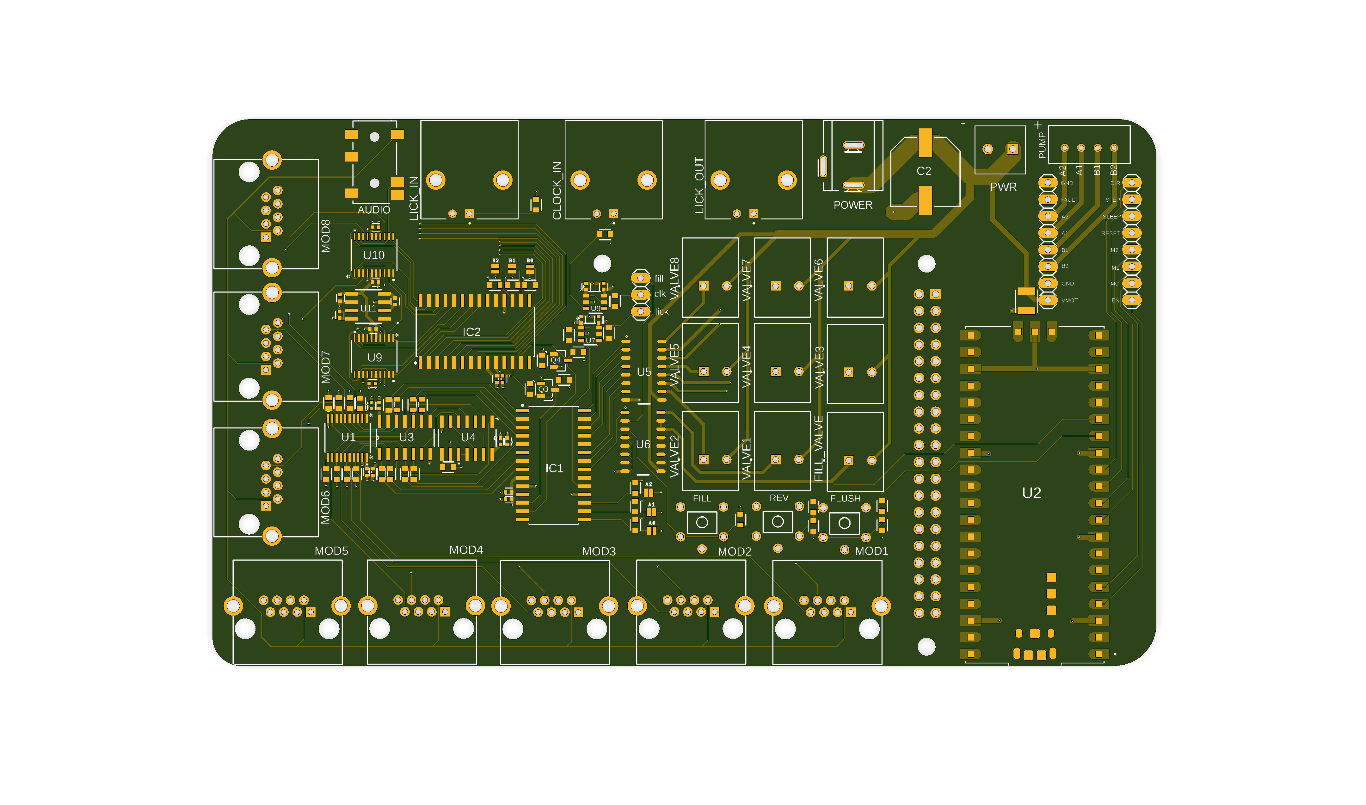
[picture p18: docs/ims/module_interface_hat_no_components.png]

2. Plug the stepper motor driver in the appropriate slot on the interface HAT being careful to match the pins correctly.
3. Now we will attach the components to the pi. The pi should be turned off at this stage. If Audio is needed plug in the audio hat first followed by the assembled interface HAT. Connect the audio hat to the interface HAT additionally by an audio cable (use the headphone jack of the audio hat). Use standoffs as needed.
4. Set all M# threaded inserts in place on the printed box parts using a soldering iron
4. Secure the Pi to the printed interface box base with M2.5 screws.
5. Screw on the back with M3 screws.
6. Power on the Pi first by plugging in the Pi power supply, then power on the Interface by plugging in the 12V supply.
7. Use a multimeter to set VREF of the stepper motor driver to 1V such that the max current output will be limited to 2A. The steps to do this are outlined [here](https://www.pololu.com/product/2133) but we will briefly note them below.

    a. Measure VREF by first placing the negative probe of the multimeter on ground (this can be accessed from the negative screw of the PWR screw terminal; you will need to screw in place a loose wire first for this to work). Place the positive terminal on the trimpot itself.
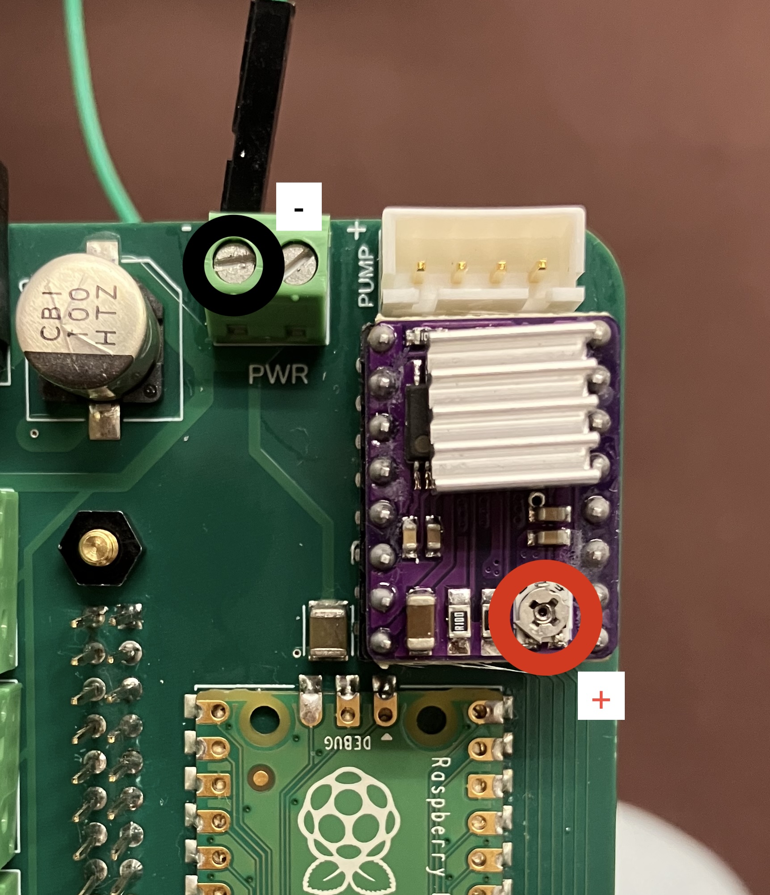
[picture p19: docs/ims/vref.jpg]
    
    b. Turn the trimpot until VREF is 1V

8. Plug in the pump. Pass the wires for any valves through the hold in the lid and plug them into their appropriate slots on the interface. 
9. Use a jumper to connect the male header pins to the appropriate GPIO pins given your config.yaml and presets.yaml file. These pins are unfortunately not labeled on the board in v1 but we show the names below:
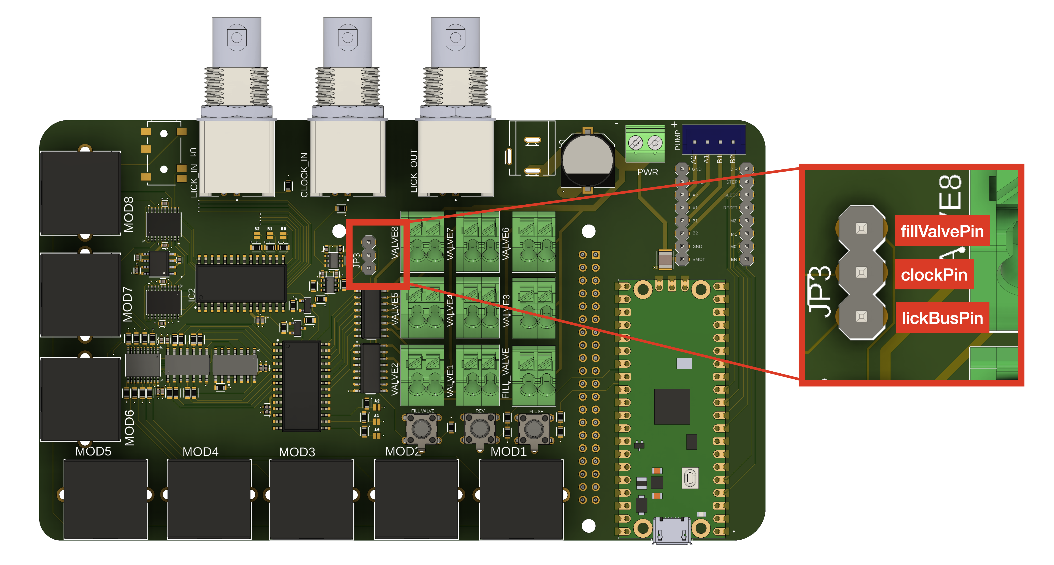
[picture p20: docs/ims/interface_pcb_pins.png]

10. Screw on the lid with M3x22mm screws being sure not to over tighten and cause damage to the PCB
11. Plug the Pico into the Raspberry Pi using a USB cable.

Once assembled you can use the flush and reverse buttons to ensure the pump is functional. Press the fill valve button to ensure this valve can be toggled by the button.

## Module Electronics
### Required Components
* Module PCB
* 0.1µF electrolytic capacitor - [C1]
* 2-pin screw terminal (x2) - [AUDIO, LED]
* [1kΩ Trim Potentiometer](https://www.digikey.com/en/products/detail/bourns-inc/PV36P102C01B00/666482) (x1) - [TRIM_LED]
* [5kΩ Trim Potentiometer](https://www.digikey.com/en/products/detail/bourns-inc/PV36P502C01B00/666496) (x1) - [TRIM_EMITTER]
* JST female connector (x1)
* Ethernet Conector (x1)
* LM6132BIN (x1) 
* 50Ω resistor (x1) - [R_TERM]
* 22kΩ resistor (x1) - [R_PHOTO]
* 68Ω resistor (x1) - [R_EMITTER]
* 220Ω resistor (x1) - [R_LED]

### Assembly Steps

*Setting up the PCB*
1. Solder all components to the PCB. The v1 module PCB is missing labels for the values of vertain components so we show them below. (*NOTE: The ethernet connector is meant to be soldered on the back of the PCB. Also, For the LM6132, the square solder pad indicates where the top left corner of the component should go*)
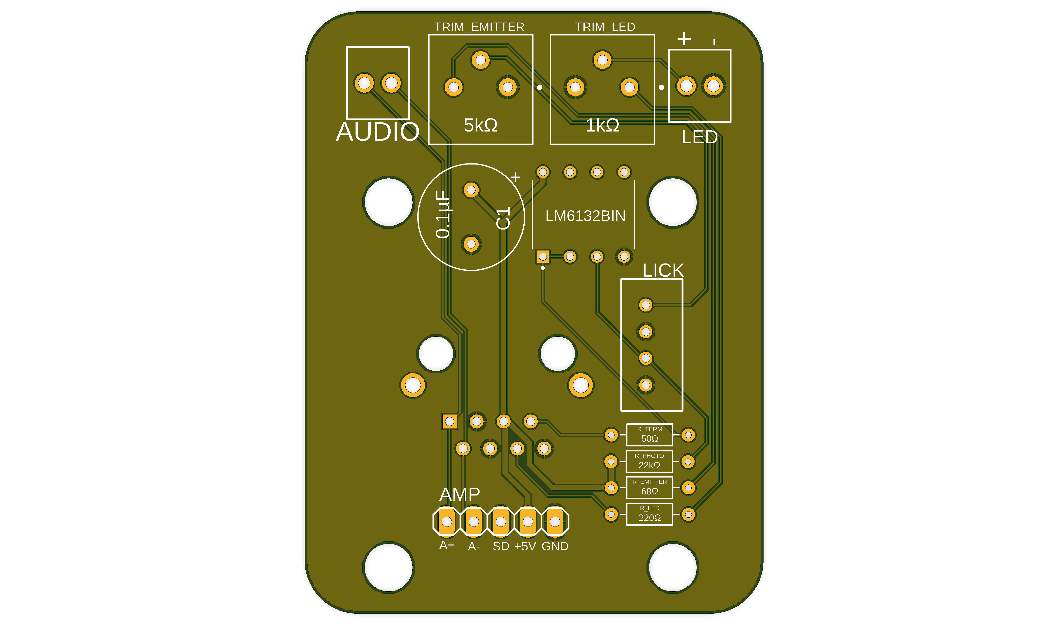
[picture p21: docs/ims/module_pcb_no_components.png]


*Setting the Lickometer Trimpot*
1. Once all other electronics have been assembled and all software has been installed, plug the assembled lickometer into the module PCB and plug the module PCB into the interface. 
2. Start the ratBerryPi server and trigger licks with an object of comparable size to a mouse or rat tongue. We usually use a small flathead screwdriver. 
3. Start with the trim_emitter potentiometer set to a fairly high resistance and lower the resistance to a point where you just start registering licks.

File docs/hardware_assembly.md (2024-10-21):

## Pump Assembly
### Required Components

*Printed Parts*
* [Pump Carriage Sled](../hardware/3Ddesigns/stl/pump_carriage_sled.stl)
* [Pump Base](../hardware/3Ddesigns/stl/pump_base.stl)
* [Syringe Clamp](../hardware/3Ddesigns/stl/pump_syringe_clamp.stl)
* [Syringe Brace](../hardware/3Ddesigns/stl/pump_syringe_brace.stl)

*Additional Pieces*
* M3 Hex Nuts (x8)
* 10 mm long M3 socket head screws (x4)
* 20 mm long M3 socket head screws (x4)
* 25 mm long M3 socket head screws (x4)
* 12 mm long M4 thumb screw (x2)
* [M4x6 threaded inserts](https://www.amazon.com/100pcs-M4-Threaded-Inserts-Components/dp/B0CZXMXZG2/ref=asc_df_B0CZXMXZG2/?tag=hyprod-20&linkCode=df0&hvadid=693637112524&hvpos=&hvnetw=g&hvrand=18070985569350448006&hvpone=&hvptwo=&hvqmt=&hvdev=c&hvdvcmdl=&hvlocint=&hvlocphy=9031119&hvtargid=pla-2355037181884&mcid=de6cd1ac120c37788256b2d3de154efd&th=1) (x2)
* M5 Hex Nut (x1)
* [50 mm long M5 Knob](https://www.amazon.com/Kipp-06220-405X50-Thermoplastic-External-Diameter/dp/B013I72QTY/ref=sr_1_6?s=industrial&ie=UTF8&qid=1513737752&sr=1-6&keywords=M5+knob) (x1)
* [150 mm long T8 Lead Screw + Nut](https://www.amazon.com/150mm（5-9-Inches）Tr8x2-Thread-Printer-Machine/dp/B0B8RGRYNW/ref=sr_1_2?crid=2PI5409AN7P8M&dib=eyJ2IjoiMSJ9.NOXkkOYI_8yEDDdQ4KmFjBWnvBEwRLslsTZclAvBnbL_KOv4d9s6TYV7Yn544udbtQOYQXvm2dr9G_Ep9ubmZK9Rg4Xr69crSYm5hNxOl-wg4prLb-qqFuYFbljIq9QVpmSEQVmfwoT48KGZFxoAb-WrPK3JdLU6P3ORKLwpgLvZrBFGSQqaKDwgmBYALRPol7djfDgh1sJT8BxapY-XdOXylolAWgHEqzAiywRl2d1UcMa3TGKzSWVdgSiVDuHt1jn8gQtWl0cUQW8XgRdSmPLsAtrViMXtH6d-Jm2j6IM.4UlREFWkPLfs1N6UiTGZtPtQ8Gy_k3MyA0ZD5ybcKd8&dib_tag=se&keywords=150mm%2Btr8x2%2Bacme%2Blead%2Bscrew%2Band%2Bbrass%2Bnut&qid=1728682639&s=industrial&sprefix=150mm%2Btr8x2%2Bacme%2Blead%2Bscrew%2Band%2Bbrass%2Bnut%2Cindustrial%2C183&sr=1-2&th=1) (x1)
* [Flexible Motor Lead Screw Coupling](https://www.amazon.com/AFUNTA-Flexible-Couplings-Compatible-Machines/dp/B07JL1QYLS/ref=pd_bxgy_thbs_d_sccl_1/141-5956694-6505548?pd_rd_w=qr3Ns&content-id=amzn1.sym.4e8180d8-1c12-4df8-af99-b6dc78fc0026&pf_rd_p=4e8180d8-1c12-4df8-af99-b6dc78fc0026&pf_rd_r=4T94AV7PVW2MM7R65NRM&pd_rd_wg=a20A0&pd_rd_r=dc5a870c-a3d4-4b0e-ba6b-15bc7fdf8f1d&pd_rd_i=B07JL1QYLS&psc=1) (x1)
* [Nema 17 Bipolar Stepper Motor](https://www.amazon.com/STEPPERONLINE-Stepper-Bipolar-Connector-compatible/dp/B00PNEQKC0) (x1)
* [Steel Rods](https://www.amazon.com/Steel-Round-Turning-Lathe-200mm/dp/B00LUSVKVY/ref=pd_sim_469_2?_encoding=UTF8&pd_rd_i=B00LUSVKVY&pd_rd_r=G7BG21YGXPVGEYXQ3GW3&pd_rd_w=WYFjR&pd_rd_wg=t8WZj&refRID=G7BG21YGXPVGEYXQ3GW3&th=1) (x2)
* [Linear Motion Ball Bearings](https://www.amazon.com/Linear-Motion-Bearing-Bushing-Printer/dp/B07K71FWMG/ref=pd_bxgy_thbs_d_sccl_2/138-0211087-8320359?pd_rd_w=7Q4QU&content-id=amzn1.sym.3858a394-39a9-4946-90e6-86a3153d2546&pf_rd_p=3858a394-39a9-4946-90e6-86a3153d2546&pf_rd_r=6N2RDYHQYJK3EC33EJZV&pd_rd_wg=J7q7j&pd_rd_r=3c87071d-28a5-4f1b-80da-199966422f73&pd_rd_i=B07K71FWMG&psc=1) (x2)
* [JST Xh 4 Pin Male Connector Pre-Assembled](https://www.amazon.com/Sets-2-5-4-Connector-200mm-Female/dp/B01DUC1S14) (x1)
* White Lithium Grease (or lubricant of your choice)

### Assembly Steps
*Assemble the carriage sled*
1. Secure the lead screw nut to the carriage sled using the 25 mm long M3 screws and hex nuts. Start by positioning the lead screw nut in its designated hole on the back of the carriage sled as shown below, then align the holes in the nut with the holes in the sled.
2. Secure the threaded M4 inserts inside the holes of the syringe clamp. Start by positioning the inserts by hand on the flat surface of the clamp, then use a soldering iron to heat up the insert and push it into the material until the front face of the insert is flush with the flat face of the clamp.
3. Attach the clamp to the carriage sled using the thumb screws.
4. Pop the linear motion ball bearings into the sides of the carriage sled.

*Secure the Motor*
1. First couple the lead screw to the motor using the flexible coupler.
2. Feed the attached lead screw through the hole on the back side of the pump base and manually rotate the lead screw to mate it with the nut in the carriage sled. Position the carriage sled approximately halfway down the length of the lead screw.
3. Use the 20mm long M3 screws to secure the motor to the base of the pump.
4. Feed the rods through the appropriate holes in the pump base.
5. Place the remaining hex nuts in the square holes shown in the image below. Slide the nuts in until you can see the hole in the middle from the screw hole.
6. Secure the rods in place with the 10mm long M3 screws through the hex nuts placed in step 5.

*Attach the Syringe Brace*
1. Drop the M5 nut in the hole shown below and thread the M5 knob through it.
2. Place the syringe brace on the end of the knob.

*Making the Connector*

We use a different connector from the one that comes with the motor to interface the motor to the pcb. This is in part to correct for a difference in the pin ordering on the connector that comes with the motor. The main reason, however, is that the connector we use instead is polarized which allows us to enforce that the pins are plugged in the correct order. The reverse order would cause the pump to move in the opposite direction of what the software expects. Below we'll describe the steps to assemble an adapter.

1. Solder the wires of the JST connector to the 4-pin male header following the arrows in the image below. Note the mapping shown in A is based on the pin map in the documentation for this motor copied in B. If in the future the mapping of pin to wire color on the motor changesm these mappings should be updated accordingly.
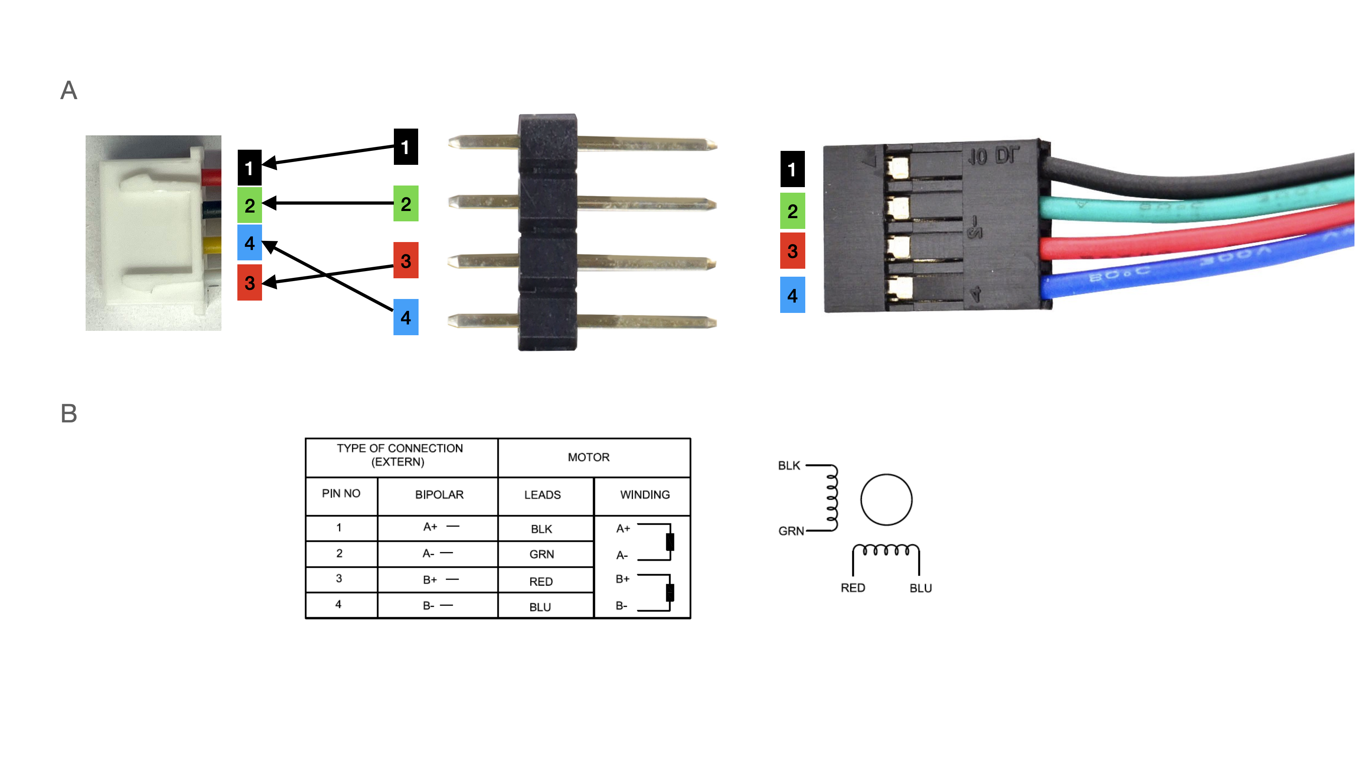
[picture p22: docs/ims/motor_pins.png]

2. Plug the adapter into the motor connector in the orientation shown in the image above.

Once the pump is fully assembled, apply white lithium grease to the threads of the lead screw and both rods. Once the electronics for the interface have been assembled, plug the pump into the interface, power on the pump (i.e. plug in the 12V power supply) and use the flush and reverse buttons to spread the grease along the length of the rods. Clear away any excess when finished.

## Manifold Assembly
### Required Components
*Printed Parts*
* Manifold Mount

*Additional Pieces*
* [Solenoid Media Isolation Valves [Clippard NR1-2-12]](https://www.clippard.com/part/NR1-2-12) (x9 or $n_{modules}$ + 1)
*  3-way luer stopcocks (x9 or $n_{modules}$ + 1)
* 1/16" ID PVC tubing
* O-Rings
* Barb Fittings
* Male Luer to Barb adapter (x20 or $(n_{valves} + 1)*2$)

### Assembly Steps
...

## Lickometer Assembly
### Required Components
*Printed Parts*
* [Mouse Lickometer](../hardware/3Ddesigns/stl/lickometer_mouse.stl) or [Rat Lickometer](../hardware/3Ddesigns/stl/lickometer_rat.stl) 

***Note about printing:*** *we recommend printing with the front of the lickometer on the print bed for these files like shown below. Furthermore if your slicer supports it, only use supports on the bed of the printer. These settings ensure there will be no supports in the channels where the sensors need to go*

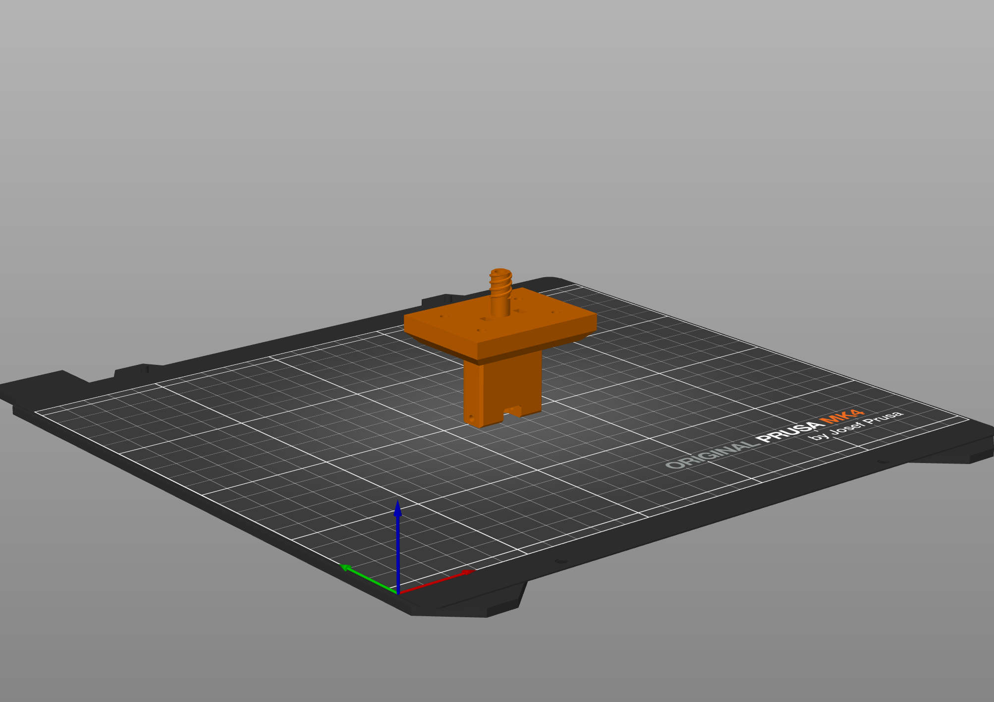
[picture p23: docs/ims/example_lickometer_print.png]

*Additional Pieces*
* IR Emitter (x1)
* IR Phototransistor (x1)
* [JST Xh 4 Pin Male Connector Pre-Assembled](https://www.amazon.com/Sets-2-5-4-Connector-200mm-Female/dp/B01DUC1S14) (x1)
* x mm long M3 set screws

### Assembly Steps
1. Solder the wires of the JST connector to the IR Emitter and Phototransistor following the below diagram
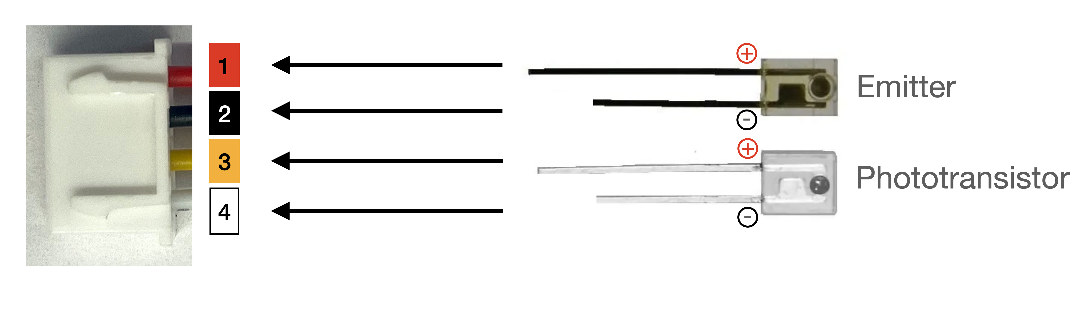
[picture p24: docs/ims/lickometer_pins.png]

2. Tap M3 threads in the holes on the sides of the lickometer and M4 threads in the holes on the back.
3. Insert either the emitter or phototransistor into one of the slots in the lickometer with the bulb facing towards the inside of the lickometer. Be careful to go only far enough such that the entire bulb is visible from the hole looking into the lickometer well. 
4. Secure the emitter or phototransistor in place using an M3 set screw.
5. Repeat steps 3 and 4 for the other component using the other slot.

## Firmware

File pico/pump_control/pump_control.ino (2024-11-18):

#include <math.h>

// enable pin
#define ENABLE_PIN 2

// microstepping pins
#define M0 3              
#define M1 6
#define M2 7

// other pins for stepping the motor
#define STEP_PIN 8
#define DIR_PIN 9

// pins for buttons used to manually control the motor
#define FLUSH 10
#define REV 11

// parameters for serial communication
#define BAUD_RATE 230400  // the rate at which data is read
// The buffer allows us to store bytes as they are read from the python program (64 bytes in size)
const byte buffSize = 64;
char inputBuffer[buffSize];
// We create inputs to this program by <...> where <> represent the startread and endread markers
const char startMarker = '<';
const char endMarker = '>';
byte bytesRecvd = 0;
bool readInProgress = false;
bool newDataFromPC = false;
char mode[buffSize] = {0};
char setting[buffSize] = {0};
float value = 0.0;
char dir[buffSize] = {0};

// order of microstep levels: {"Full", "Half", "1/4", "1/8", "1/16", "1/32"};
const int microsteps_per_rev[6] = {200, 400, 800, 1600, 3200, 6400};
const bool microstep_settings[6][3] = {
  {false, false, false},
  {true, false, false},
  {false, true, false},
  {true, true, false},
  {false, false, true},
  {true, false, true}
};
int curr_microstep_lvl;

//parameters for stepping the motor and keeping track of position
int direction = 1;               // direction to move the piston (+1 for forward -1 for backward)
unsigned long steps_to_go = 0;   // number of microsteps left to complete the current move
unsigned long step_interval;     // inter-step interval in microseconds (computed when calling setSpeed(speed))
unsigned long speed;             // motor speed in microsteps per second
unsigned long last_step;         // time in microseconds since boot of the last step of the motor
const float lead = 0.2;          // lead of the lead screw in cm
float position = 0;              // position of the piston in cm
float cmPerStep;                 // cm traveled by the piston per microstep (computed when setting the microstep level)
float distance;                  // requested distance to move the piston
int running = 0;                 // whether or not the pump is currently running (1 if running 0 if not)
bool running_manual = false;     // whether or not the pump is being controlled manually
float pulse_width = 5;           // width of pulses used to step the motor in microseconds

unsigned long last_log;          // time since boot in milliseconds of the last log
int log_interval = 100;          // time interval in milliseconds between logs
int moveCompleted = 1;           // flag to be raised when a move has been completed and cleared (set to 0) before the start of a move

void setup() {


  Serial.begin(BAUD_RATE);

  //step dir, and enable pins
  pinMode(ENABLE_PIN, OUTPUT);
  pinMode(STEP_PIN, OUTPUT);
  pinMode(DIR_PIN, OUTPUT);
  digitalWrite(ENABLE_PIN, HIGH);
  digitalWrite(DIR_PIN, LOW);
  digitalWrite(STEP_PIN, LOW);


  // Set microstep pins
  pinMode(M0, OUTPUT);
  pinMode(M1, OUTPUT);
  pinMode(M2, OUTPUT);

  set_microstep_lvl(0);
  setSpeed(1000);

  // Set initial speed and acceleration
  pinMode(FLUSH, INPUT);
  pinMode(REV, INPUT);

  last_log = millis();
  last_step = micros();
}

void loop() {

  bool to_flush = digitalRead(FLUSH);
  bool to_rev = digitalRead(REV);

  if (running!=1 && (to_flush || to_rev)){
    if (to_rev) {direction = -1;}
    else {direction = 1;}
    setTarget(10000);
    running_manual = true;
  } else if (running_manual && !(to_flush || to_rev)){
    stop();
  }

  step();
  getDataFromPC();

  if ((millis() - last_log) >= log_interval){
    Serial.print(position);
    Serial.print(",");
    Serial.print(running);
    Serial.print(",");
    Serial.print(direction);
    Serial.print(",");
    Serial.print(moveCompleted);
    Serial.print(",");
    Serial.print(curr_microstep_lvl);
    Serial.print(",");
    Serial.println(speed);
    last_log = millis();
  }
}

void step(){

  // check if the motor is due for a microstep and if so step
  // similar to the run method of AccelStepper
  // thist should be called as frequently as possible

  if ((running==1) && (steps_to_go>0)){
    if((micros() - last_step) >= step_interval){
      digitalWrite(DIR_PIN, direction == 1);
      digitalWrite(STEP_PIN, HIGH);
      last_step = micros();
      delayMicroseconds(pulse_width);
      digitalWrite(STEP_PIN, LOW);
      position -= direction * cmPerStep;
      steps_to_go -= 1;
      if (steps_to_go==0){
        digitalWrite(ENABLE_PIN, HIGH);
        running=0;
        moveCompleted = 1;
      }
    }
  }
}

void stop(){
  // stop any currently running pump tasks
  steps_to_go = 0;
  digitalWrite(ENABLE_PIN, HIGH);
  running = 0;
  running_manual = false;
}

void setTarget(unsigned long target){
  // set the target number of microsteps for the motor
  steps_to_go = target;
  if (target > 0){
    digitalWrite(ENABLE_PIN, LOW);
    running = 1;
    }
  last_step = micros();
}

void setSpeed(float _speed){
  // set the speed that the motor will step
  float _step_interval = 1000000/_speed;
  if (_step_interval > (100 * pulse_width)){
    step_interval = _step_interval;
    speed = _speed;
  }
}

void set_microstep_lvl(int microstep_lvl){
   if ((microstep_lvl < sizeof(microsteps_per_rev)) && (microstep_lvl>=0)) {
    if (running==1){
      // if the motor is currently moving update the number of microsteps to go
      // so the motor reaches the same target
      float conversion = float(microsteps_per_rev[microstep_lvl])/float(microsteps_per_rev[curr_microstep_lvl]);
      steps_to_go = round(steps_to_go*conversion);
    }
    curr_microstep_lvl = microstep_lvl;
   }
   cmPerStep = get_cmPerStep();
   update_microstep_pins();
}

void update_microstep_pins(){
  digitalWrite(M0, microstep_settings[curr_microstep_lvl][0]);
  digitalWrite(M1, microstep_settings[curr_microstep_lvl][1]);
  digitalWrite(M2, microstep_settings[curr_microstep_lvl][2]);
}

float get_cmPerStep(){
  return lead/microsteps_per_rev[curr_microstep_lvl];
}

// the following is adapted from the original poseidon code
void getDataFromPC() {

  // If there is data from the serial port
  if (Serial.available() > 0) {
    // read a single character
    char x = Serial.read();

    // the order of these IF clauses is significant
    if (x == endMarker) {
      readInProgress = false;
      newDataFromPC = true;
      // clear the buffer
      inputBuffer[bytesRecvd] = 0;
      // and parse the data
      return parseData();
    }

    if (readInProgress) {
      // add the character to the buffer
      inputBuffer[bytesRecvd] = x;
      bytesRecvd ++;
      if (bytesRecvd == buffSize) {
        bytesRecvd = buffSize - 1;
      }
    }

    if (x == startMarker) {
      bytesRecvd = 0;
      readInProgress = true;
    }
  }
}

//=============

/*
  # <Mode, Setting, Value>
  # Mode can be SETTING, RUN, STOP, CALIBRATE, CLEAR 
  # Setting can be SPEED, MICROSTEP
*/

// Here is where we take the string <...> that we have read from the serial port and parse it
void parseData() {

  // split the data into its parts
  // strtok scans the string inputBuffer until it reaches a "," or a ">"
  // Then we declare the variable associated with that part of the inputBuffer
  // each strtok contiues where the previous call left off

  char * strtokIndx; // this is used by strtok() as an index

  strtokIndx = strtok(inputBuffer, ",");     // get the first part - the mode string
  strcpy(mode, strtokIndx);                  // copy it to messageFromPC

  strtokIndx = strtok(NULL, ",");            // get the second part - the setting string
  strcpy(setting, strtokIndx);               // copy it to messageFromPC

  strtokIndx = strtok(NULL, ",");            // get the fourth part - the value float
  value = atof(strtokIndx);                  // convert to float and copy to value

  strtokIndx = strtok(NULL, ",");            // get the fifth part - the direction character
  strcpy(dir, strtokIndx);                   // copy the character to dire

  strtokIndx = strtok(NULL, ",");            // get the fourth part - the value float
  distance = atof(strtokIndx);                // convert to float and copy to value

  newDataFromPC = true;
  return executeThisFunction();
  }

// =============================
// So we do a string comparison using strcmp(str1, str2) as a condition to determine what to do next
// Here we can add new functions if we like, for example if we wanted to add a "TEST" to the mode
// input we would add a condition if (strcmp(mode, "TEST") == 0 {...}
void executeThisFunction() {

  if (strcmp(mode, "STOP") == 0) {stop();}

  else if (strcmp(mode, "SETTING") == 0) {udpateSettings();}

  else if (strcmp(mode, "RUN") == 0) {
    // Check if any stepper is currently running and do not allow execution if that is the case
    if (running_manual){stop();}
    if (running == 0) {
      direction = 1;
      if (strcmp(dir, "B") == 0) {
        direction = -1;
      }
      setTarget(int(round(distance/cmPerStep)));
    }
  }
  else if (strcmp(mode, "CALIBRATE") == 0) {
    position = 0;
  }
  else if (strcmp(mode, "CLEAR") == 0){
    moveCompleted = 0;
  }
}

void udpateSettings() {
  if (strcmp(setting, "SPEED") == 0) {
    setSpeed(value);
  }
  else if (strcmp(setting, "MICROSTEP") == 0) {
    set_microstep_lvl(value);
  }
}

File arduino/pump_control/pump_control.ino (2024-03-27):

#include <AccelStepper.h>
#include <math.h>
#include <EEPROM.h>

// Define stepper motor connections and steps per revolution
#define BAUD_RATE 230400  // the rate at which data is read
#define M0 2
#define M1 3
#define M2 4
#define STEP_PIN 5
#define DIR_PIN 6
#define FLUSH 8
#define REV 9
#define POS_SAVE_IDX 0

// Create stepper motor object
AccelStepper stepper(AccelStepper::DRIVER, STEP_PIN, DIR_PIN);

// The buffer allows us to store bytes as they are read from the python program (64 bytes in size)
const byte buffSize = 64;
char inputBuffer[buffSize];
// We create inputs to this program by <...> where <> represent the startread and endread markers
const char startMarker = '<';
const char endMarker = '>';

byte bytesRecvd = 0;
bool readInProgress = false;
bool newDataFromPC = false;
char mode[buffSize] = {0};
char setting[buffSize] = {0};
float value = 0.0;
char dir[buffSize] = {0};

// order of microstep levels: {"Full", "Half", "1/4", "1/8", "1/16", "1/32"};
const int microsteps_per_rev[6] = {200, 400, 800, 1600, 3200, 6400};
const bool microstep_settings[6][3] = {
  {false, false, false},
  {true, false, false},
  {false, true, false},
  {true, true, false},
  {false, false, true},
  {true, false, true}
};
const float pitch = 0.08;
int curr_microstep_lvl;

int direction = 1;
float position; // position of the piston in cm
float cmPerStep;
float distance;
bool running_manual = false;

unsigned long t;
int log_interval = 50;

void setup() {


  Serial.begin(BAUD_RATE);

  EEPROM.get(POS_SAVE_IDX, position);

  // Set microstep pins
  pinMode(M0, OUTPUT);
  pinMode(M1, OUTPUT);
  pinMode(M2, OUTPUT);

  set_microstep_lvl("Full");

  // Set initial speed and acceleration
  stepper.setMaxSpeed(1000); // Adjust the speed according to your requirement
  stepper.setAcceleration(5000.0); // Adjust the acceleration according to your requirement

  pinMode(FLUSH, INPUT);
  pinMode(REV, INPUT);

  t = millis();
}

void loop() {
  bool to_flush = digitalRead(FLUSH);
  bool to_rev = digitalRead(REV);
  if (stepper.isRunning()==0 && (to_flush || to_rev)){
    if (to_rev) {direction = -1;}
    else {direction = 1;}
    stepper.move(direction * 10000);
    running_manual = true;
  }
  else if (running_manual && !(to_flush || to_rev)){
    stepper.stop();
    running_manual = false;
  }
  if (stepper.isRunning()==1){
    stepper.run();
    position = -stepper.currentPosition() * cmPerStep;
  }
  else {
    EEPROM.put(POS_SAVE_IDX, position);
  }
  getDataFromPC();
  if ((millis() - t) >= log_interval){
    Serial.print(position);
    Serial.print(",");
    Serial.print(stepper.isRunning());
    Serial.print(",");
    Serial.println(direction);
    t = millis();
  }
}

void set_microstep_lvl(int microstep_lvl){
   if ((microstep_lvl < sizeof(microsteps_per_rev)) && (microstep_lvl>=0)) {
    curr_microstep_lvl = microstep_lvl;
   }
   cmPerStep = get_cmPerStep();
   update_microstep_pins();
}

void update_microstep_pins(){
  digitalWrite(M0, microstep_settings[curr_microstep_lvl][0]);
  digitalWrite(M1, microstep_settings[curr_microstep_lvl][1]);
  digitalWrite(M2, microstep_settings[curr_microstep_lvl][2]);
}

float get_cmPerStep(){
  return pitch/microsteps_per_rev[curr_microstep_lvl];
}

void calibrate(){
  float prev_speed = stepper.maxSpeed();
  stepper.setCurrentPosition(0);
  stepper.setMaxSpeed(prev_speed);
  position = -stepper.currentPosition() * cmPerStep;
  EEPROM.put(POS_SAVE_IDX, position);
}


// the following is adapted from the original poseidon code
void getDataFromPC() {

  // If there is data from the serial port
  if (Serial.available() > 0) {
    // read a single character
    char x = Serial.read();

    // the order of these IF clauses is significant
    if (x == endMarker) {
      readInProgress = false;
      newDataFromPC = true;
      // clear the buffer
      inputBuffer[bytesRecvd] = 0;
      // and parse the data
      return parseData();
    }

    if (readInProgress) {
      // add the character to the buffer
      inputBuffer[bytesRecvd] = x;
      bytesRecvd ++;
      if (bytesRecvd == buffSize) {
        bytesRecvd = buffSize - 1;
      }
    }

    if (x == startMarker) {
      bytesRecvd = 0;
      readInProgress = true;
    }
  }
}

//=============

/*
  # <Mode, Setting, Value>
  # Mode can be SETTING, RUN, STOP
  # Setting can be SPEED, ACCEL, DELTA, ONE, FEW, ALL, ZERO
  # Pump number can be 1 or 2 or 3 or 12 or 13 or 23. (## indicates two pumps to run)
*/
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

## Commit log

2023-03-09 mv files to utils, make syringe class general
2023-04-25 expose port for other devices to connect to server
2023-04-27 code for testing the pump
2023-07-12 rm extra socket bind
2023-07-19 rm utils
    [87265K13_Electrically Conductive Easy-to-Form ABS-PVC.stl, pump_base.stl, pump_carriage_sled.stl]
2023-07-19 print errors in broadcast
2023-08-11 more audio functions
    [lickometer_inner.stl, lickometer_outer.stl]
2023-08-15 default led state is off
2023-08-16 intermittently fill syringe
2023-08-19 start readme; make lickometer a plugin
    [87265K13_Electrically Conductive Easy-to-Form ABS-PVC.stl, lickometer_inner.stl, lickometer_outer.stl, pump_base.stl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]
2023-08-28 log the pump state
2023-08-29 changed some pins; switch to 50 ms init delay for valves
2023-09-08 add intermittent refilling when filling a line
    [pump_carriage_sled_tail.stl]
2023-09-08 fix pump gpios in config; fix relative imports
2023-09-26 make sure is_open is a property in valve
2023-09-26 make sure to close fill valve before reward
2023-09-26 reopen fill valve when filling
2023-10-10 start trying to allow refill during triggered pump
2023-10-23 start implementing thread locks for sync
2023-10-24 clean up server shutdown; make valve release lock
2023-10-25 make sure outlet valve is set to NO
2023-10-25 add input checking to avoid pressure build up
2023-11-15 clean up stop seq for pump threads; rm reply log
2023-11-15 specify syringes by vol instead of max_pos
2023-11-27 change direction syntax; multiple MCP23017s
    [lickometer.stl, pump_carriage_sled.stl]
2023-12-01 forgot to uncomment starting of autofill thread
2023-12-09 add electronics
    [87265K13_Electrically Conductive Easy-to-Form ABS-PVC.stl, lickometer.stl, lickometer_inner.stl, lickometer_outer.stl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]
2023-12-09 add pcb manufacturing files
    [BOM_module_interface v103_2023-12-08.csv, BOM_module_pcb_v54_2023-12-08.csv, PickAndPlace_module_interface v103_2023-12-08.csv, copper_bottom.gbr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]
2023-12-09 finalize pcb build
    [BOM_module_interface v103_2023-12-08.csv, BOM_module_pcb_v54_2023-12-08.csv, FINAL_BOM-2023-12-09.xls, FINAL_BOM_2023-12-09.xls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]
2023-12-10 clean up the files for jlcpcb
    [FINAL_BOM-2023-12-09.xls, FINAL_BOM_2023-12-09.xls, FINAL_BOM_module_interface-2023-12-09.xls, FINAL_BOM_module_pcb_2023-12-09.xls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]
2023-12-11 round corners of module pcb
    [FINAL_BOM_module_pcb_2023-12-09.xls, INITIAL_EASYEDA_BOM_module_pcb_v75_2023-12-09.csv, PickAndPlace_module_pcb_v75_2023-12-09.csv, PickAndPlace_module_pcb_v78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]
2023-12-15 added headers for motor driver
    [FINAL_BOM_module_interface-2023-12-09.xls, INITIAL_EASYEDA_BOM_module_interface v106_2023-12-09.csv, INITIAL_EASYEDA_BOM_module_interface_v108_2023-12-11.csv, 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]
2024-01-09 readme updates
    [back_wall.dxf, front_wall.dxf, side_wall.dxf, wall_mounted_module.dxf]
2024-01-09 update port mapping to reflect pcbs
2024-01-25 speed up refilling; fix fill valve and pump reservation issues
2024-01-25 log step delay
    [FINAL_BOM_module_interface-2023-12-09.xls, FINAL_BOM_module_interface-2023-12-14.xls, drill_1_16.xln]
2024-03-06 emit pyqtsignal on lick and pump move; add dependencies to setup.py; update readme
2024-03-25 some arduino code for pump
2024-03-27 add support for arduino controlled pump
2024-03-28 use pico instead of arduino
2024-04-12 pcb revisions
    [FINAL_BOM_module_interface-2023-12-14.xls, FINAL_BOM_module_pcb_2023-12-09.xls, INITIAL_EASYEDA_BOM_module_interface_v108_2023-12-11.csv, INITIAL_EASYEDA_BOM_m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]
2024-04-13 moveCompleted flag for pico pump; new cli
2024-05-25 custom stepper control code
2024-05-25 make pico pump main pump; set speed/microstep from interface
2024-08-02 new board design
    [copper_bottom.gbr, copper_top.gbr, drill_1_16.xln, gerber_job.gbrjob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]
2024-08-03 update build files
    [jlcpcb_bom.xls, module_interface_hat v88.csv, module_interface_hat_v58.brd, pnp_module_interface_hat v88.csv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]
2024-08-04 fix gerber files for interface hat (missing layers)
    [copper_bottom_l4.gbr, copper_inner_l2.gbr, copper_inner_l3.gbr, copper_top_l1.gbr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]
2024-08-12 updated build files
    [module_interface_hat_v58.brd, module_interface_hat_v90.brd, pnp_module_interface_hat v90.csv, pump_base.stl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]
2024-08-13 update jlcpcb part number for logic translator
    [module_interface_hat v88.csv]
2024-08-22 update pin mapping in pico code
2024-08-29 configure lick interrupt pin as active high instead of open drain based on new pcb
2024-09-05 update imports in cli to still work on remote devices
2024-10-11 some assembly instructions
2024-10-14 move v0 stuff to archive; document assembly of the pump (TODO: need more pics)
    [FINAL_BOM_module_interface-2023-12-14.xls, FINAL_BOM_module_pcb_2023-12-09.xls, INITIAL_EASYEDA_BOM_module_interface_v108_2023-12-11.csv, INITIAL_EASYEDA_BOM_m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]
2024-10-15 more assembly docs
    [lickometer_rat.stl]
2024-10-15 update pcb picture
2024-10-15 interface electronics assembly
2024-10-16 start on module pcb assembly instructions
2024-10-21 add box and manifold mount stls and instructions for box assembly
    [2valve_mount.stl, back_wall.dxf, front_wall.dxf, interface+audio_box_back.stl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]
2024-10-26 make wall of box base thinner near connectors
    [interface+audio_box_base.stl, interface_box_base.stl]
2024-11-18 make pump sleep when not in use
2025-02-16 updated electronics design files
    [copper_bottom_l4.gbr, copper_inner_l2.gbr, copper_inner_l3.gbr, copper_top_l1.gbr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]
2025-03-19 updated pump carriage sled and clamp stl
    [pump_carriage_sled.stl, pump_syringe_clamp.stl]
2025-04-07 update default auto fill threshold; print error in mL; pump more on change direction to accomodate slack; wait for pumps to initialize on start
